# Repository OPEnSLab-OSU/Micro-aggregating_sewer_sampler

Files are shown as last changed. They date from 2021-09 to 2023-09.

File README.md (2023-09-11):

# Micro-Aggregating Sewer Sampler (MASS)
Compositing autosampler using weight based sampling targeted for sewage sampling in manholes. Code originally housed in 1232 branch of [SingleSampler repository](https://github.com/OPEnSLab-OSU/SingleSampler) and created using [Kawin Pechetratanapanit's sampler framework](https://github.com/OPEnSLab-OSU/OPEnSamplerFramework). Instructions for setting up PlatformIO within Visual Studio code are provided in the [OPEnSampler Framework Getting Started Guide](https://opensampler-framework.readthedocs.io/en/latest/pages/start_here.html). 



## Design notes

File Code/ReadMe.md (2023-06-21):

Getting Started
-----------------
This code is an application of the OPEnSamplerFramework. The easiest way to start using OPEnSamplerFramework is to use VSCode with PlatformIO extension. 
See [Getting Started Guide](https://opensampler-framework.readthedocs.io/en/latest/pages/start_here.html).

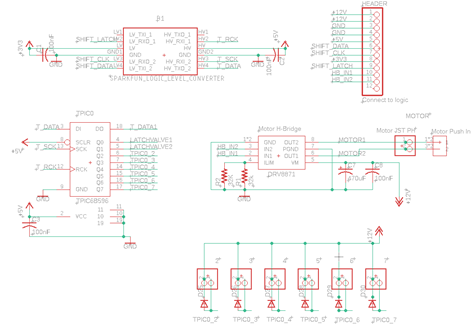
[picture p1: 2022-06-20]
DesignFiles/Power_module_schematic.png

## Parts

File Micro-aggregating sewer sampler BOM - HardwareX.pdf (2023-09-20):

Designator | Component | Number | Cost per unit $

Minimum
purchase
quantity

Total
cost $

Source of
materials

Material
type
| | Enclosures - Device
Cooler | 10 gal watercooler | 1 | $49.89 | 1 | $49.89 | Homedepot (https://www.homedepot.com/p/The-Home-Depot-10-Gal-Orange-Water-Cooler-FG1610HDORAN/202260809?) | Other
Tube holder | 3D printed tube holder | 1 | $0.19 | 1 | $0.19 | Zenodo (https://doi.org/10.5281/zenodo.8333206) | Polymer
Epoxy | Loctite 1919324 Marine Epoxy | 1 | $7.74 | 1 | $7.74 | Amazon (https://www.amazon.com/dp/B00KH62K50?amp&amp) | Polymer
Corner Brace | 2 in galvanized corner brace with screws | 4 | $1.62 | 4 | $6.46 | Home Depot (https://www.homedepot.com/p/Everbilt-2-in-Galvanized-Corner-Brace-4-Pack-15267/202033914) | Metal
Star drive screw | 3/4" 18-8 stainless steel screw | 8 | $0.42 | 25 | $10.59 | Amazon (https://www.amazon.com/Stainless-Thread-Rolling-Plastic-Passivated/dp/B00GDYW2TY) | Metal
1/2" PVC coupler | 1/2" schedule 40 PVC coupler | 1 | $0.67 | 1 | $0.67 | Home Depot (https://www.homedepot.com/p/Charlotte-Pipe-1-2-in-PVC-Schedule-40-S-x-S-Coupling-PVC021000600HD/203811331) | Polymer
Buckles | Adjustable Quick Side Release Buckles | 2 | $1.05 | 4 | $4.21 | Amazon (https://www.amazon.com/gp/product/B07N6B4CR5/ref=ppx_yo_dt_b_search_asin_title?ie=UTF8&psc=1) | Polymer
Webbing | Heavyweight Polypropylene Webbing 2 inch | 1 | $1.22 | 30 ft | $36.57 | Amazon (https://www.amazon.com/gp/product/B01KTVCGJ2/ref=ppx_yo_dt_b_search_asin_title?ie=UTF8&psc=1) | Polymer
Drawer slides | Heavy Duty Drawer Slides 14 inch | 2 | $28.40 | 2 | $56.80 | Amazon (https://www.amazon.com/AOLISHENG-Bearing-Capacity-Extension-Runners/dp/B08BKPTFQ7) | Composite
L bracket | Aluminum 90° Angle - 3.5" height, 1/4" thick | 1 | $21.27 | 1 | $21.27 | McMaster Carr (https://www.mcmaster.com/8982K137-8982K276/) | Metal
5 mm washers | 5 mm Stainless Steel Washers | 8 | $0.31 | 4 | $2.50 | Home Depot (https://www.homedepot.com/p/Everbilt-5-mm-Stainless-Steel-Flat-Washer-4-Pieces-01228/202209491) | Metal
Flathead bolt | M5, 16 mm long bolt | 6 | $0.24 | 100 | $24.00 | McMaster Carr (https://www.mcmaster.com/91430A326/) | Metal
Lock nut | M5 lock nut | 6 | $0.63 | 2 | $3.75 | Home Depot (https://www.homedepot.com/p/Everbilt-M5-0-8-Stainless-Steel-Lock-Nut-2-Pieces-D42-H-837181/321071796) | Metal
Acrylic Sheet | Acrylic - clear 24" x 24", 1/8" | 1 | $26.08 | 1 | $26.08 | McMaster Carr (https://www.mcmaster.com/8560K259/) | Polymer
Large ice pack | Reusable Ice Pack, 1 Large | 3 | $7.38 | 4 | $29.52 | Amazon (https://www.amazon.com/dp/B07YX7TCJP/ref=twister_B07YX7T91Y?_encoding=UTF8&th=1) | Composite
Medium ice pack | Reusable Ice Pack, 1 Medium | 2 | $3.79 | 4 | $15.16 | Amazon (https://www.amazon.com/dp/B07YX7TCJP/ref=twister_B07YX7T91Y?_encoding=UTF8&th=1) | Composite
Cable with carabiner | Stainless Steel Safety Cable Lock | 3 | $2.40 | 4 | $7.19 | Amazon (https://www.amazon.com/Stainless-Ekunbuy-Security-Carabiner-Flexible/dp/B08GZ6PDGY) | Metal
1/8" wire rope | Stainless steel wire rope, 1/8" | 1 | $0.54 | 33 ft | $17.88 | Amazon (https://www.amazon.com/Railing-VIGRUE-Stainless-Aluminum-Sleeves/dp/B08HN1J894) | Metal
Battery | 12 Volt 7.2 Ah SLA battery | 1 | $17.50 | 1 | $17.50 | Amazon (https://www.amazon.com/ML7-12-Battery-Mighty-Brand-Product/dp/B00K8V30D0) | Other
Quick-Disconnect Terminal | Quick-Disconnect Terminal | 2 | $1.08 | 1 | $2.16 | McMaster Carr (https://www.mcmaster.com/72625K21/) | Composite
Paracord | 1/8" x 50 ft paracord | 1 | $0.11 | 50 ft | $5.48 | Home Depot (https://www.homedepot.com/p/Everbilt-1-8-in-x-50-ft-Assorted-Color-Paracord-Rope-MFP350/205517109) | Polymer
Hydraulics - Pump
Peristaltic Pump | Peristaltic Pump DC 6Vto 24V | 1 | $54.64 | 1 | $54.64 | Aliexpress (https://www.aliexpress.com/item/4001286485389.html?spm=a2g0s.9042311.0.0.87964c4dVvskfj) | Other
Pump tubing | Hi-Temp Silicone Rubber Tubing | 1 | $1.39 | 10 ft | $13.90 | McMaster Carr (https://www.mcmaster.com/5236K891/) | Polymer
Tube to hose stem | 3/8" to 3/8" Tube To Hose Stem | 1 | $2.39 | 10 | $23.93 | Home Depot (https://www.homedepot.com/p/John-Guest-3-8-in-Push-to-Connect-Tube-to-Hose-Stem-Fitting-10-Pack-PP251212W/206940472) | Polymer
Cable tie | Cable tie, 0.1" width, 4" length | 2 | $0.04 | 100 | $3.59 | McMaster Carr (https://www.mcmaster.com/7130K52/) | Polymer
Elbow push-to-connect | 3/8 OD x 3/8 OD elbow push-to-connect | 1 | $1.30 | 10 | $12.99 | Amazon (https://www.amazon.com/dp/B07NQ8BXP3?s=hi&sp_csd=d2lkZ2V0TmFtZT1zcF9kZXRhaWw) | Composite

Designator | Component | Number | Cost per unit $ | Minimum purchase quantity | Total cost $ | Source of materials | Material type
Elbow barbed | Barbed elbow, 3/8" OD | 1 | $1.02 | 1 | $1.02 | McMaster Carr (https://www.mcmaster.com/5463K596-2974K237/?s=barbed+fittings) | Polymer
3/8" tubing | Soft ND-100-65 Tygon PVC Tubing | 1 | $93.00 | 25 ft | $93.00 | McMaster Carr (https://www.mcmaster.com/8349T26/) | Polymer
Small snap-grip clamps | Snap-Grip Clamp 29/64" to 9/16" Clamp ID | 2 | $0.46 | 25 | $11.40 | McMaster-Carr (https://www.mcmaster.com/5246K84/) | Polymer
Faraday Fabric | EMF shielding Film | 1 | $23.00 | 44"W x 36"L | $23.00 | Amazon (https://www.amazon.com/Shielding-Bluetooth-Blocking-Military-Conductive/dp/B01M294MGK) | Other
Electrical tape | Electrical tape | 1 | $5.98 | 66 ft | $5.98 | Home Depot (https://www.homedepot.com/p/Scotch-Super-33-3-4-in-x-66-ft-x-0-007-in-Vinyl-Electrical-Tape-Black-6132-BA-10/304653556) | Polymer
M3 bolt - 16 mm | 16mm M3 screw low profile | 9 | $0.13 | 100 | $13.16 | McMaster Carr (https://www.mcmaster.com/90666A107/) | Metal
M3 washer - 9 mm | 18-8 Stainless Steel Oversized Washer M3 | 13 | $0.05 | 100 | $4.93 | McMaster Carr (https://www.mcmaster.com/91116A120/) | Metal
M3 nuts | M3 nuts stainless steel | 9 | $0.06 | 50 | $3.03 | McMaster Carr | Metal
Barbed tee fitting | Barbed tee fitting, 3/8" OD | 1 | $1.40 | 10 | $13.95 | McMaster Carr (https://www.mcmaster.com/5463K608-2974K249/) | Polymer
Quick-Disconnect Plug to 3/8" barbed | Plug, 1/4 Size, for 3/8" Barbed Tube ID | 1 | $4.11 | 1 | $4.11 | McMaster Carr (https://www.mcmaster.com/5923K72/) | Polymer
Quick-Disconnect Socket to 3/8" barbed | Socket, 1/4 Size, for 3/8" Barbed Tube ID | 1 | $5.58 | 1 | $5.58 | McMaster Carr (https://www.mcmaster.com/5923K42/) | Polymer
Polyethylene tubing | Polyethylene Tube, Shore D: 45, 1/4 in ID | 1 | $4.10 | 10 ft | $4.10 | Grainger (https://www.grainger.com/product/USA-SEALING-Tubing-Polyethylene-55YU87?searchQuery=55YU87&searchBar=true) | Polymer
Tee push-to-connect | 3/8" OD Tee push-to-connect | 1 | $1.10 | 10 | $10.99 | Amazon (https://www.amazon.com/Tailonz-Pneumatic-Plastic-Connect-Fittings/dp/B07R2CQKKJ?c=ts&rnid=23957419011&s=industrial&ts_id=580146011) | Composite
Hydraulics - Valves
Motorized Ball valve - normally closed | Motorized Ball valve 1/4'' NPT - auto return | 2 | $38.29 | 1 | $76.58 | Amazon (https://www.amazon.com/Motorized-Valve-Stainless-U-S-Solid/dp/B06XXPZHVB) | Other
PTFE tape | PTFE tape | 1 | $0.98 | 260 in. | $0.98 | Home Depot (https://www.homedepot.com/p/Harvey-1-2-in-x-260-in-Thread-Sealing-PTFE-Plumber-s-Tape-0178503/202280370) | Polymer
Straight 3/8” push to connect to ¼ NPT | 3/8"OD push to connect x 1/4 Inch NPT | 2 | $1.80 | 10 | $17.99 | Amazon (https://www.amazon.com/dp/B07PN3P2PN/ref=twister_B08DR6ZB7S?_encoding=UTF8&psc=1) | Composite
Barbed 3/8" elbow to 1/4" NPT Male | Barbed elbow 3/8" ID x 1/4 NPT Male | 1 | $2.73 | 1 | $2.73 | McMaster Carr (https://www.mcmaster.com/5047K37/) | Polymer
Elbow 3/8" push-to-connect to 1/4" NPT | 3/8 OD elbow push-to-connect to 1/4 NPT | 1 | $1.88 | 5 | $9.39 | Amazon (https://www.amazon.com/Metalwork-Plastic-Nickel-Connect-Fitting/dp/B07F8YZ456) | Composite
Valve bracket | 3D printed valve bracket | 2 | $0.41 | 1 | $0.81 | Zenodo (https://doi.org/10.5281/zenodo.8333206) | Polymer
Large snap-grip clamps | Snap-Grip Clamp 37/64" to 41/64" Clamp ID | 1 | $0.49 | 25 | $12.17 | McMaster Carr (https://www.mcmaster.com/5246K86/) | Polymer
PVC tubing | PVC Firm tubing 1/4 ID 3/8 OD | 1 | $16.80 | 25 ft | $16.80 | McMaster Carr (https://www.mcmaster.com/1487T2/) | Polymer
Straight 3/8" push to connect fitting | Straight 3/8" push to connect fitting | 1 | $3.81 | 1 | $3.81 | McMaster Carr (https://www.mcmaster.com/5562K421/) | Composite

Hydraulics - Sample bag
Mylar Bag | 3L Mylar Bag | 1 | $0.89 | 250 | $221.80 | IMPAK (https://www.impakcorporation.com/flexible_packaging/CSP0912BG04) | Other
Threaded valved coupler | Coupler, Push In, Acetal, White | 1 | $6.08 | 1 | $6.08 | CPC (https://products.cpcworldwide.com/en_US/ProductsCat/APC/APCD10006) | Polymer
Eye bolt and nut | Eye bolt and nuts | 1 | $0.69 | 2 | $1.38 | Home Depot (https://www.homedepot.com/p/Everbilt-8-32-tpi-x-1-5-8-in-Zinc-Plated-Steel-Eye-Bolts-with-Nuts-2-Piece-per-Pack-816671/204273506) | Metal

Designator | Component | Number | Cost per unit $ | Minimum purchase quantity | Total cost $ | Source of materials | Material type
Barbed elbow coupling insert | Coupler, Push In, Acetal, White | 1 | $1.40 | 1 | $1.40 | CPC (https://products.cpcworldwide.com/en_US/ProductsCat/APC/APC23006) | Polymer
1/16" wire rope | 1/16" wire rope | 1 | $0.98 | 1 ft | $0.98 | Home Depot (https://www.homedepot.com/p/Everbilt-1-16-in-x-1-ft-Stainless-Steel-Uncoated-Wire-Rope-809786/204765202) | Metal
Compression sleeve | 1/16" Wire Rope Compression Sleeve | 1 | $0.97 | 10 | $9.69 | McMaster-Carr (https://www.mcmaster.com/3755T13/) | Metal
Load Cell Mechanical
M5 bolt | M5 bolt, 40 mm | 1 | $1.38 | 2 | $1.38 | Home Depot (https://www.homedepot.com/p/Everbilt-M5-0-8-x-40-mm-Phillips-Pan-Head-Stainless-Steel-Machine-Screw-2-Pack-843098/204283788) | Metal
Large Washer | 18 mm OD M5 washer | 2 | $0.14 | 100 | $14.29 | McMaster Carr (https://www.mcmaster.com/98363A111/) | Metal
Neoprene washer | 1/4" thick neoprene washer | 2 | $0.69 | 4 | $2.75 | Home Depot (https://www.homedepot.com/p/Everbilt-1-4-in-x-5-8-in-Black-Neoprene-Washer-4-Pieces-89188/100338046) | Polymer
Spacer | Spacer - 7 mm | 1 | $1.76 | 1 | $1.76 | McMaster Carr (https://www.mcmaster.com/94669A334/) | Metal
M5 nut | M5 stainless steel nut | 1 | $0.63 | 2 | $1.25 | Home Depot (https://www.homedepot.com/p/5-mm-8-Hex-Nut-Stainless-862608/323370947) | Metal
Enclosures - Electronics
Electronic Box | Polycarbonate waterproof box | 1 | $5.88 | 1 | $5.88 | Arrow (https://www.arrow.com/en/products/rb55p14c10g/serpac-electronic-enclosures?q=RB55P14C10G) | Polymer
RGB LED | WS2812B LED | 1 | $0.16 | 100 | $15.99 | Amazon (https://www.amazon.com/gp/product/B01D1FFVOA/ref=ppx_yo_dt_b_search_asin_title?ie=UTF8&psc=1) | Composite
LED box | LED 3D printed box | 1 | $0.04 | 1 | $0.04 | OPEnS | Polymer
LED lid | LED 3D printed lid | 1 | $0.05 | 1 | $0.05 | OPEnS | Polymer
3 wire cable | 3 wire cable | 1 | $0.31 | 100 ft | $31.10 | Amazon (https://www.amazon.com/Custom-Cable-Connection-Conductor-Stranded/dp/B071DFHKRB) | Composite
Super glue | Gorilla Super Glue Gel | 1 | $6.84 | 1 | $6.84 | Amazon (https://www.amazon.com/dp/B082XGL21J?amp=undefined) | Polymer
Push button | Momentary Push button waterproof | 2 | $2.20 | 5 | $10.99 | Amazon (https://www.amazon.com/gp/product/B07F9PLSRY/ref=ppx_yo_dt_b_search_asin_title?ie=UTF8&psc=1) | Composite
2 pin JST wire pairs | 2 pin JST wire pairs | 4 | $1.60 | 5 | $7.99 | Amazon (https://www.amazon.com/JST-XH-Balance-Connector-Silicone-Woodland/dp/B07YKHV46N?cv_ct_cx=jst-xh+wire+2+pin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) | Composite
Small heat shrink | Small heat shrink | 4 | $0.01 | 580 | $6.59 | Amazon (https://www.amazon.com/gp/product/B01MFA3OFA/ref=ppx_yo_dt_b_search_asin_title?ie=UTF8&psc=1) | Polymer
Solder seal connectors | Solder Seal Wire Connectors 22-18 AWG | 4 | $0.20 | 50 | $9.99 | Amazon (https://www.amazon.com/gp/product/B07C3MKM3K/ref=ppx_yo_dt_b_search_asin_title?ie=UTF8&th=1) | Composite
PG7 cable gland | PG7 cable gland | 1 | $1.52 | 1 | $1.52 | Mouser (https://www.mouser.com/ProductDetail/Hammond-Manufacturing/1427NCGPG7B?qs=sGAEpiMZZMvSvAwuKVmiP9gF42NFqy3rmTmaMc262xA%3D) | Polymer
PG13.5 cable gland | PG13.5 cable gland | 1 | $1.89 | 1 | $1.89 | Mouser (https://www.mouser.com/ProductDetail/Hammond-Manufacturing/1427NCGPG13B?qs=l4Gc20tDgJJFw57NH75JRw%3D%3D) | Polymer
Power plug | Right Angle Power Plug Jack to Bare Wire | 1 | $1.60 | 10 | $15.99 | Amazon (https://www.amazon.com/gp/product/B0851CV1Y6/ref=ppx_yo_dt_b_search_asin_title?ie=UTF8&psc=1) | Composite
microUSB cable | Right angle microUSB cable | 1 | $5.58 | 1 | $5.58 | DigiKey (https://www.digikey.com/en/products/detail/qualtek/3021079-06/8681882) | Other
Stranded wire: black, red, white, green | 22 AWG Gauge Stranded Wire, 6 colors | 1 | $1.25 | 6 rolls at 5 ft | $7.50 | Amazon (https://www.amazon.com/Fermerry-Stranded-Electrical-Silicone-Cables/dp/B089CQ2N69) | Composite
Power Module PCB Components
Power module PCB | Power module mini PCB | 1 | $2.30 | 5 | $11.50 | Zenodo (https://doi.org/10.5281/zenodo.8333206) | Composite
Logic level converter | Sparkfun logic level shifter | 1 | $2.95 | 1 | $2.95 | Sparkfun (https://www.sparkfun.com/products/12009) | Composite

Designator | Component | Number | Cost per unit $ | Minimum purchase quantity | Total cost $ | Source of materials | Material type
12 pin angle female header | 12 pins angle female header | 1 | $0.80 | 1 | $0.80 | DigiKey (https://www.digikey.com/product-detail/en/sullins-connector-solutions/PPTC121LGBN-RC/S5448-ND/775906) | Composite
32K resistor | Resistor 32K Ohm 3.3mm | 1 | $0.10 | 1 | $0.20 | DigiKey (https://www.digikey.com/product-detail/en/stackpole-electronics-inc/CF18JT33K0/CF18JT33K0CT-ND/2022778) | Other
470uF capacitor | Capacitor 470uF SMD 16V | 1 | $0.51 | 1 | $0.51 | DigiKey (https://www.digikey.com/product-detail/en/nichicon/UWT1C471MNL1GS/493-2181-1-ND/590156) | Other
100 nF capacitor | Capacitor 100nF SMD | 4 | $0.12 | 1 | $0.48 | DigiKey (https://www.digikey.com/product-detail/en/samsung-electro-mechanics/CL31B104KBCNNNC/1276-1017-1-ND/3889103) | Other
Flyback Diode | Diode Standard 100V 150 mA | 2 | $0.15 | 1 | $0.30 | DigiKey (https://www.digikey.com/product-detail/en/diodes-incorporated/1N4148W-7-F/1N4148W-FDICT-ND/815280) | Other
Shift register | IC Power 8-bit shift Register 20-SOIC | 1 | $1.42 | 1 | $5.68 | DigiKey (https://www.digikey.com/product-detail/en/texas-instruments/TPIC6B595DWR/296-1351-1-ND/404964) | Other
Relay | 1 Channel DC 5V Relay Module | 1 | $1.75 | 1 | $6.99 | Amazon (https://www.amazon.com/gp/product/B095YD3732/ref=ppx_yo_dt_b_search_asin_title?ie=UTF8&psc=1) | Other
Standoff | M3 standoff | 1 | $2.17 | 1 | $2.17 | McMaster Carr (https://www.mcmaster.com/98952A112/) | Metal
M3 6 mm bolt | M3 6 mm bolt | 1 | $0.05 | 50 | $2.51 | Grainger (https://www.grainger.com/product/GRAINGER-APPROVED-Socket-Head-Cap-Screw-M3-0-22TY43) | Metal
Rectifier Diode | Rectifiers Diode, DO-41, 50V, 1A | 1 | $0.40 | 1 | $0.40 | Mouser (https://www.mouser.com/ProductDetail/Diotec-Semiconductor/1N4001?qs=OlC7AqGiEDlll8NA510wmA%3D%3D) | Other
Logic Module Components
Logic pcb | Logic Module PCB | 1 | $2.30 | 5 | $11.50 | Zenodo (https://doi.org/10.5281/zenodo.8333206) | Composite
M0 female header | Feather M0 header female | 1 | $0.95 | 1 | $0.95 | Adafruit (https://www.adafruit.com/product/2886) | Composite
Angle male header | Angle male header 2.54 mm | 12 | $0.02 | 1 | $0.24 | DigiKey (https://www.digikey.com/products/en?keywords=HDR100IMP40M-G-RA-TH-ND) | Composite
MicroSD mount | MicroSD card mount SMD - Hinged type | 1 | $1.16 | 1 | $1.16 | DigiKey (https://www.digikey.com/product-detail/en/molex/0472192001/WM6698CT-ND/3044147) | Metal
MicroSD card | 16 GB microSD card with adapter | 1 | $7.99 | 1 | $7.99 | Amazon (https://www.amazon.com/gp/product/B004ZIENBA/ref=ox_sc_act_title_1?smid=ATVPDKIKX0DER&psc=1) | Other
Coin cell battery holder | 12mm Battery holder | 1 | $1.30 | 1 | $1.30 | DigiKey (https://www.digikey.com/product-detail/en/mpd-memory-protection-devices/BC501SM-TR/BC501SM-TRCT-ND/5418194) | Metal
Coin cell battery | CR1220 | 1 | $0.52 | 1 | $0.52 | Grainger (https://www.grainger.com/product/GRAINGER-APPROVED-1220-54ZU79) | Other
Barrel jack | Power Barrel Connector Jack Surface Mount | 1 | $1.32 | 1 | $1.32 | DigiKey (https://www.digikey.com/product-detail/en/cui-inc/PJ-002AH-SMT-TR/CP-002AHPJCT-ND/669692) | Composite
Switch | Slide switch DPDT 300MA 6V | 1 | $0.55 | 1 | $0.55 | DigiKey (https://www.digikey.com/product-detail/en/c-k/JS202011JCQN/CKN10723CT-ND/6137637) | Composite
RTC | RTC I2C 16-SOIC DS3231 | 1 | $9.78 | 1 | $9.78 | DigiKey (https://www.digikey.com/en/products/detail/maxim-integrated/DS3231SN-T-R/1197577) | Other
P-channel MOSFET | P-channel MOSFET 130mA | 1 | $0.27 | 1 | $0.27 | DigiKey (https://www.digikey.com/product-detail/en/diodes-incorporated/BSS84-7-F/BSS84-FDICT-ND/717844) | Other
Not-Gate | Inverter IC 1 Channel - SOT-23-5 | 1 | $0.34 | 1 | $0.34 | DigiKey (https://www.digikey.com/en/products/detail/texas-instruments/SN74AHC1G04DBVR/276357) | Other
D Flipflop | D Flip Flop SOT23-6 | 1 | $0.37 | 1 | $0.37 | DigiKey (https://www.digikey.com/product-detail/en/texas-instruments/SN74LVC1G175DBVR/296-17617-1-ND/706599) | Other
Zener Diode | Zener Diode 4.3 V 800 mW - Surface Mount | 1 | $0.44 | 1 | $0.44 | DigiKey (https://www.digikey.com/en/products/detail/vishay-semiconductor-diodes-division/BZD27C4V3P-E3-08/6680647) | Other
Diode Schottky | Diode Schottky 1A (DC) Surface Mount | 1 | $0.39 | 1 | $0.39 | DigiKey (https://www.digikey.com/en/products/detail/onsemi/NSR0320MW2T1G/1218949) | Other
Inductor | Inductor 10uH 2,7A | 1 | $1.69 | 1 | $1.69 | DigiKey (https://www.digikey.com/product-detail/en/wurth-electronics-inc/74438357100/732-11206-1-ND/6833665) | Other
Linear regulator | Buck regulator | 1 | $2.77 | 1 | $2.77 | TI (https://www.ti.com/product/LMR16006Y-Q1/part-details/LMR16006YQ5DDCRQ1?keyMatch=LMR16006YQ5DDCRQ1&tisearch=search-everything&usecase=OPN&login-check=true) | Other

Designator | Component | Number | Cost per unit $ | Minimum purchase quantity | Total cost $ | Source of materials | Material type
Red LED | KingBright Red LED low current 0805 | 1 | $0.51 | 1 | $0.51 | DigiKey (https://www.digikey.com/product-detail/en/kingbright/APT2012LSECK-J3-PRV/754-1935-1-ND/5177465) | Other
Yellow LED | KingBright Yellow LED low current 0805 | 1 | $0.51 | 1 | $0.51 | DigiKey (https://www.digikey.com/product-detail/en/lite-on-inc/LTL-4291N/160-1968-ND/3198548) | Other
3K resistor | Resistor 3K Ohm resistor 1% | 1 | $0.10 | 1 | $0.10 | DigiKey | Other
6.2K resistor | Resistor 6.2K Ohm 1% 1206 | 1 | $0.10 | 1 | $0.10 | DigiKey (https://www.digikey.com/product-detail/en/yageo/RC1206FR-076K2L/311-6.20KFRCT-ND/731963) | Other
10K resistor | Resistor 10k Ohm 1% 1206 | 3 | $0.10 | 1 | $0.30 | DigiKey (https://www.digikey.com/product-detail/en/te-connectivity-passive-product/CRGCQ1206J10K/A130183CT-ND/8578015) | Other
10K through hole resistor | 10k Ohm through hole resistor 1% | 2 | $0.10 | 1 | $0.20 | DigiKey (https://www.digikey.com/en/products/detail/stackpole-electronics-inc/RNMF14FTC10K0/1683930) | Other
39K resistor | Resistor 39K Ohm 5% 1206 | 1 | $0.10 | 1 | $0.10 | DigiKey (https://www.digikey.com/product-detail/en/yageo/RC1206JR-0739KL/311-39KERCT-ND/732237) | Other
100K resistor | Resistor 100K Ohm 1% 1206 | 1 | $0.10 | 1 | $0.10 | DigiKey (https://www.digikey.com/product-detail/en/yageo/RC1206FR-07100KL/311-100KFRCT-ND/731439) | Other
300K resistor | Resistor 300K Ohm 0.1% 1206 | 1 | $0.66 | 1 | $0.66 | DigiKey (https://www.digikey.com/product-detail/en/panasonic-electronic-components/ERA-8AEB304V/P300KBCCT-ND/3069731) | Other
1M resistor | Resistor 1M Ohm 0.1% 1206 | 1 | $0.62 | 1 | $0.62 | DigiKey (https://www.digikey.com/product-detail/en/stackpole-electronics-inc/RNCS1206BKE1M00/RNCS1206BKE1M00CT-ND/1801449) | Other
0.1uF 1206 capacitor | Capacitor 0.1uF 100V 1206 | 5 | $0.19 | 1 | $0.95 | DigiKey (https://www.digikey.com/en/products/detail/yageo/CC1206KKX7R0BB104/2833794) | Other
10uF 1206 capacitor | Capacitor 10uF 25V 1206 | 1 | $0.22 | 1 | $0.22 | DigiKey (https://www.digikey.com/product-detail/en/samsung-electro-mechanics/CL31A106KAHNNNE/1276-1075-1-ND/3889161) | Other
47uF 1206 capacitor | Capacitor 47uF 10V 1206 | 1 | $0.69 | 1 | $0.69 | DigiKey (https://www.digikey.com/product-detail/en/samsung-electro-mechanics/CL31A476MPHNNNE/1276-3063-1-ND/3891149) | Other
30k ohm resistor | 30k ohm resistor 5% | 1 | $0.10 | 1 | $0.10 | DigiKey (https://www.digikey.com/product-detail/en/panasonic-electronic-components/ERJ-8GEYJ303V/P30KECT-ND/203313) | Other
Load Cell Circuit
ADS1232 | 24-bit ADC | 1 | $16.99 | 1 | $16.99 | Amazon (https://www.amazon.com/NOYITO-ADS1232-Digital-Converter-Arduino/dp/B07PQW6W1L) | Other
ADS1232 interface PCB | ADS1232 interface PCB | 1 | $3.83 | 3 | $11.49 | Zenodo (https://doi.org/10.5281/zenodo.8333206) | Other
4 position terminal block | Terminal Block 4 Position Top Entry 2.54mm | 1 | $1.52 | 1 | $1.52 | DigiKey (https://www.digikey.com/en/products/detail/te-connectivity-amp-connectors/1-2834015-4/5872943) | Composite
Female Header Set | 12-pin and 16-pin Female Header Set | 1 | $0.95 | 1 | $0.95 | Adafruit (https://www.adafruit.com/product/2886) | Composite
Ferrite Bead | Ferrite Bead 300 Ohm 0805 1LN | 2 | $0.19 | 1 | $0.38 | DigiKey (https://www.digikey.com/en/products/detail/laird-signal-integrity-products/MI0805L301R-10/806751) | Other
47 uF 0805 Capacitor | Capacitor Ceramic 47uF 10V X5R 0805 | 2 | $1.25 | 1 | $2.50 | DigiKey (https://www.digikey.com/en/products/detail/kyocera-avx/0805ZD476MAT2A/13981891) | Other
0.1 uF 0805 Capacitor | Capacitor Ceramic 0.1uF 10V X7R 0805 | 2 | $0.18 | 1 | $0.36 | DigiKey (https://www.digikey.com/en/products/detail/kemet/C0805C104K8RACTU/3471722) | Other
1uF X7R 0805 Capacitor | Capacitor ceramic 1uF 10V X7R 0805 | 2 | $0.29 | 1 | $0.58 | DigiKey (https://www.digikey.com/en/products/detail/kemet/C0805C105K8RACAUTO/3314925?s=N4IgTCBcDaIMwE4EFoBsC4EZnYHIBEQBdAXyA) | Other
10 Ohm resistor | Resistor SMD 10 Ohm 0.1% 1/4W 0805 | 1 | $0.96 | 1 | $0.96 | DigiKey (https://www.digikey.com/en/products/detail/stackpole-electronics-inc/RNCF0805AKT10R0/1711294) | Other
113 Ohm Resistor | Resistor SMD 113 Ohm 0.1% 1/4W 0805 | 2 | $0.69 | 1 | $1.38 | DigiKey (https://www.digikey.com/en/products/detail/te-connectivity-passive-product/2-2176091-9/4034807) | Other
Male Jumper Wires 150 mm | Male Jumper Wires 150 mm | 1 | $0.10 | 20 | $1.95 | Adafruit (https://www.adafruit.com/product/1957) | Composite
Load Cell | Micro Load Cell (0-5Kg) | 1 | $7.00 | 1 | $7.00 | Phidgets (https://www.phidgets.com/?tier=3&catid=9&pcid=7&prodid=224) | Other
Pressure Sensor

Designator | Component | Number | Cost per unit $ | Minimum purchase quantity | Total cost $ | Source of materials | Material type
Pressure sensor PCB | Pressure sensor PCB | 1 | $0.50 | 3 | $1.50 | Zenodo (https://doi.org/10.5281/zenodo.8333206) | Composite
Pressure Sensor | Pressure Sensor MS5803-02BA | 1 | $10.72 | 1 | $10.72 | DigiKey (https://www.digikey.com/product-detail/en/te-connectivity-measurement-specialties/MS580302BA01-00/223-1624-5-ND/5277629) | Other
0.1 uF Capacitor | 0.1 uF Capacitor 1206 | 1 | $0.20 | 1 | $0.20 | DigiKey (https://www.digikey.com/product-detail/en/yageo/CC1206KKX7R0BB104/311-1488-1-ND/2833794) | Other
Pressure sensor box lid | Pressure sensor box lid | 1 | $0.07 | 1 | $0.07 | Zenodo (https://doi.org/10.5281/zenodo.8333206) | Polymer
Pressure sensor box | Pressure sensor box | 1 | $0.18 | 1 | $0.18 | Zenodo (https://doi.org/10.5281/zenodo.8333206) | Polymer
4 conductor shielded wire | 4 conductor shielded wire | 1 | $5.98 | 1 m | $5.98 | DigiKey (https://www.digikey.com/en/products/detail/tensility-international-corp/30-00452/7928047) | Composite
1/4" OD polyethylene tube | Crack-Resistant Polyethylene Firm Tubing | 1 | $3.25 | 25 ft | $3.25 | McMaster Carr (https://www.mcmaster.com/5181k39) | Polymer
Conformal coating | Conformal coating | 1 | $17.00 | 1 | $17.00 | Amazon (https://www.amazon.com/MG-Chemicals-422C-Silicone-Conformal/dp/B08K9CC5LC) | Other
Feather M0
Feather M0 | Feather M0 Basic Proto | 1 | $19.95 | 1 | $19.95 | Adafruit (https://www.adafruit.com/product/2772) | Other
M0 stacking header | Feather M0 header stacking | 1 | $1.25 | 1 | $1.25 | Adafruit (https://www.adafruit.com/product/2830) | Composite
M0 female header | Feather M0 header female | 1 | $0.95 | 1 | $0.95 | Adafruit (https://www.adafruit.com/product/2886) | Composite

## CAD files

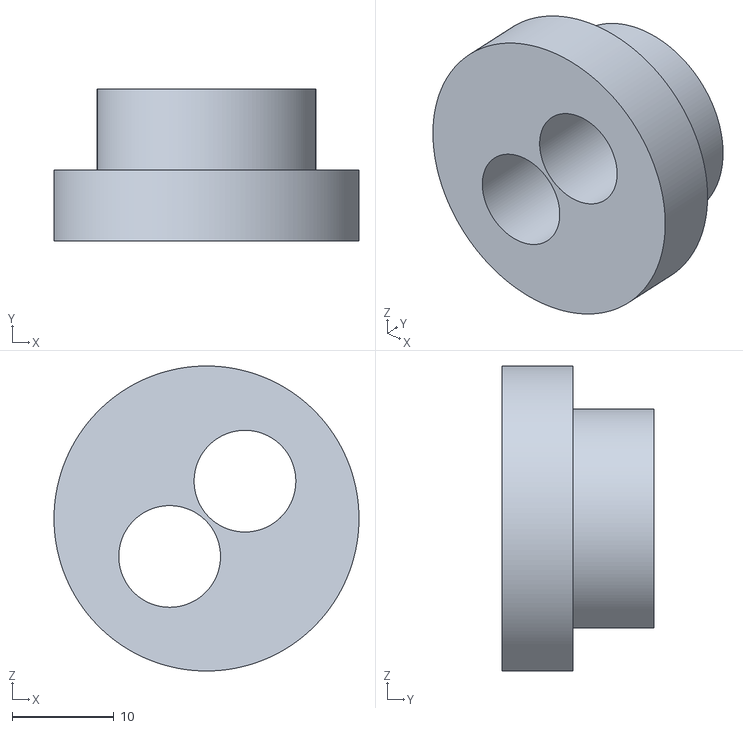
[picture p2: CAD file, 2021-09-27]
DesignFiles/Tube holder.stl
30.0 x 15.0 x 30.0

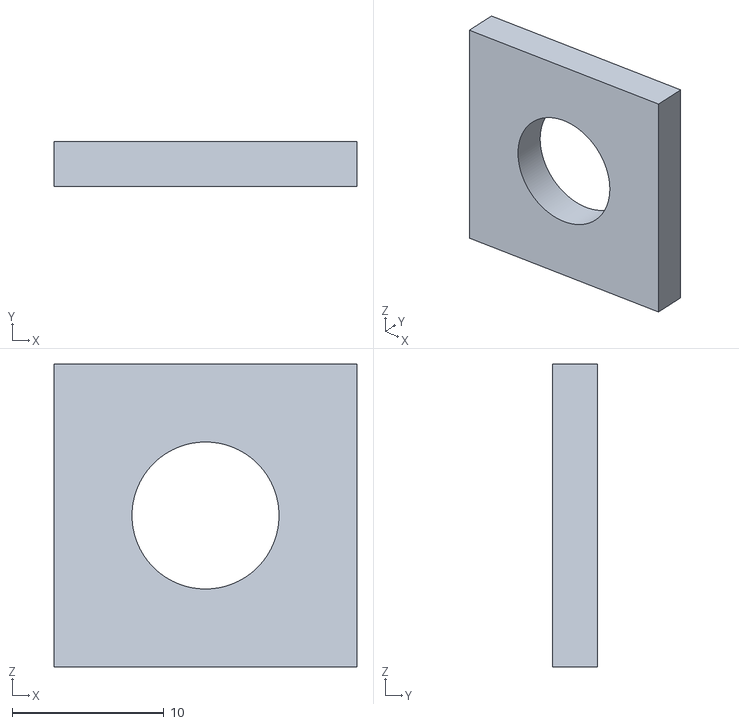
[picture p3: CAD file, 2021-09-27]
DesignFiles/LED Box.stl
20.0 x 3.00 x 20.0

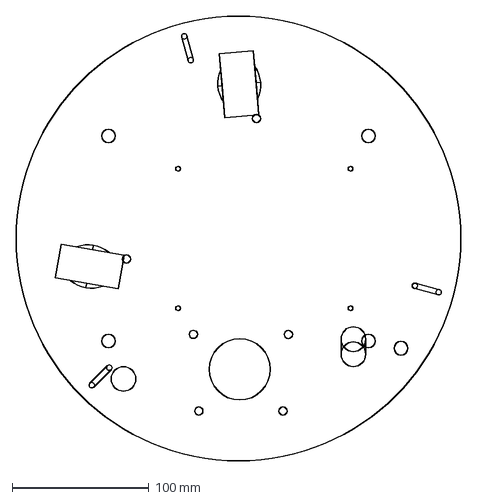
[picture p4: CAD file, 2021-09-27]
DesignFiles/AcrylicCircle.dxf
325.0 x 325.0 mm

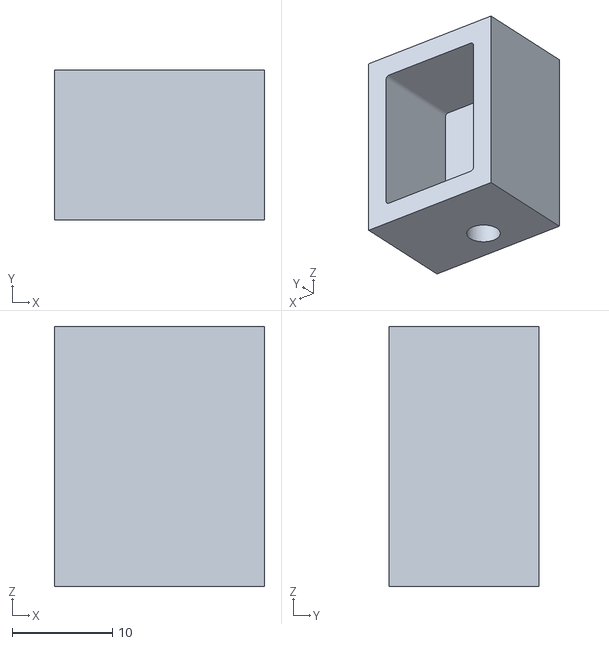
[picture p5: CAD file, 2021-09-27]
DesignFiles/pressure sensor Box.stl
21.0 x 15.0 x 26.0

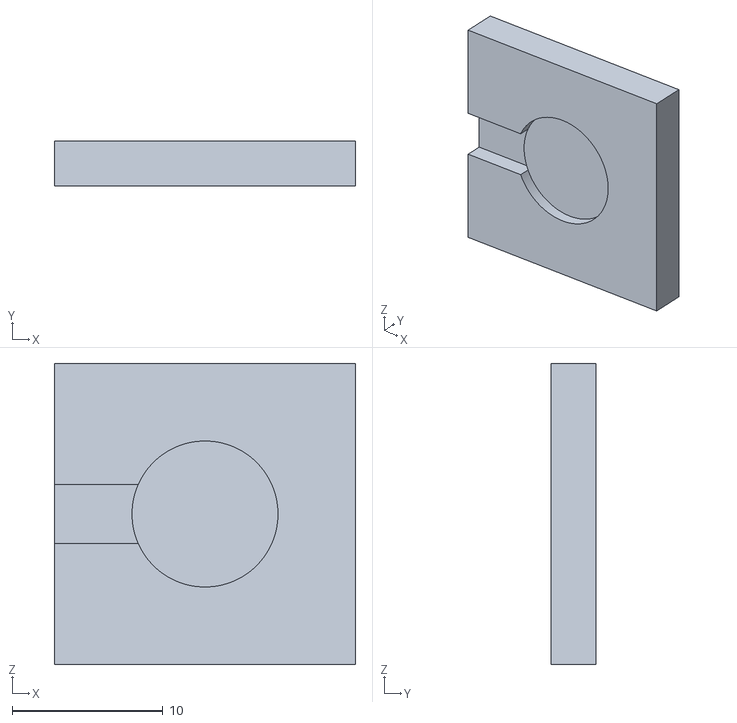
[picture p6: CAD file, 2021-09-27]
DesignFiles/LED Lid.stl
20.0 x 3.00 x 20.0

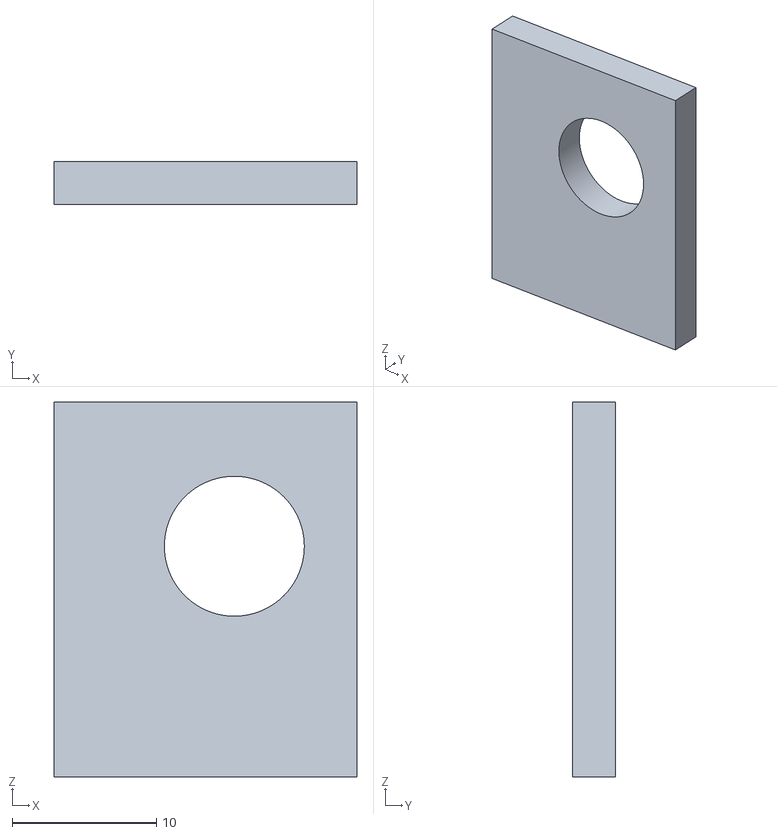
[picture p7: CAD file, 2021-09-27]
DesignFiles/pressure sensor Box lid.stl
21.0 x 3.00 x 26.0

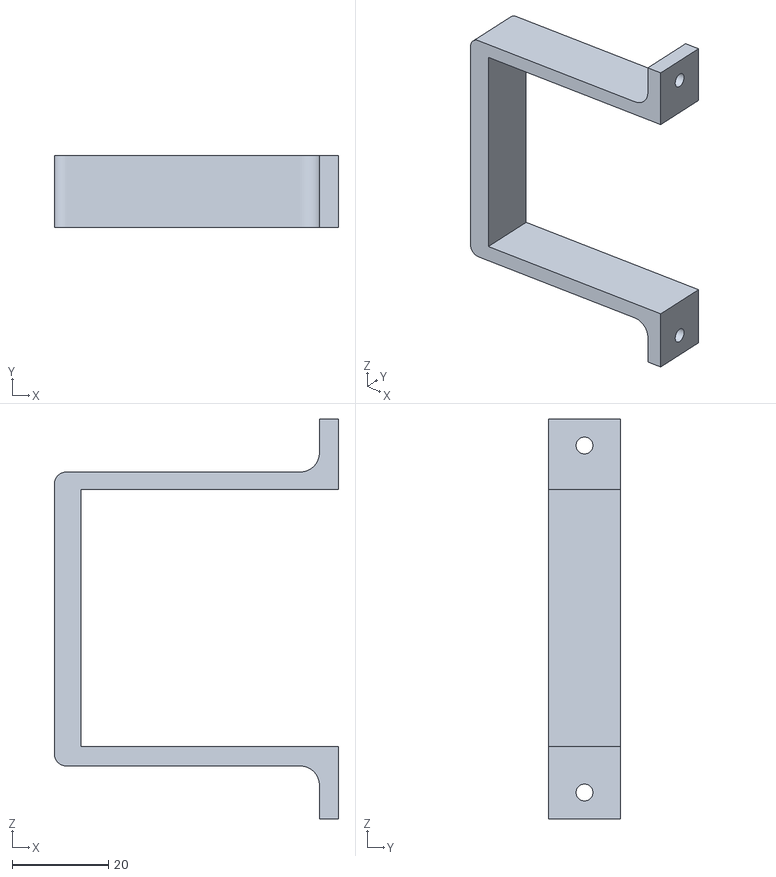
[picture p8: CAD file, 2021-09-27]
DesignFiles/Valve Bracket.stl
59.0 x 15.0 x 83.0

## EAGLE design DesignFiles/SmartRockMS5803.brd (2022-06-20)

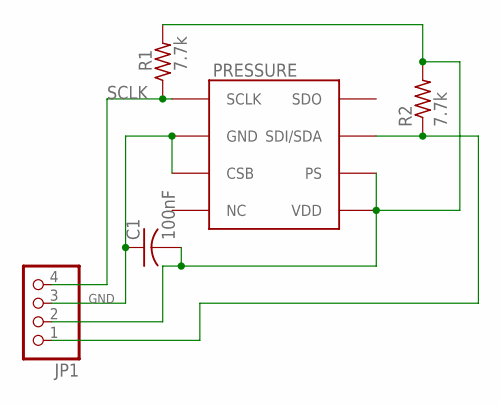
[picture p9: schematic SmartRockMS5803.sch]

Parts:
C1: 100nF; C0805
JP1: PINHD-1X4; 1X04
PRESSURE: MS5803-01BA; SMD
R1, R2: 7.7k; R0805

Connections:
GND: C1.1, JP1.3, PRESSURE.CSB, PRESSURE.GND
unnamed: C1.2, JP1.2, PRESSURE.PS, PRESSURE.VDD, R1.2, R2.2
unnamed: JP1.1, PRESSURE.SDI/SDA, R2.1
SCLK: JP1.4, PRESSURE.SCLK, R1.1

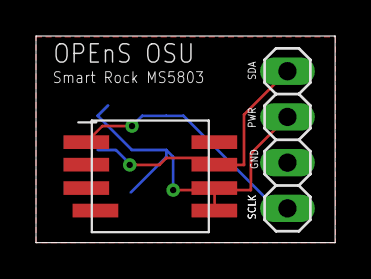
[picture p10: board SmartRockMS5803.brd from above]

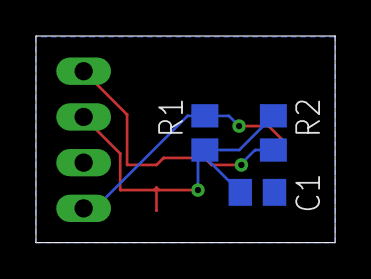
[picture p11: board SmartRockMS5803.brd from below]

Board: 2 copper layers, 16.6 x 11.5 mm, 5 parts (3 on the bottom side), 4 nets.

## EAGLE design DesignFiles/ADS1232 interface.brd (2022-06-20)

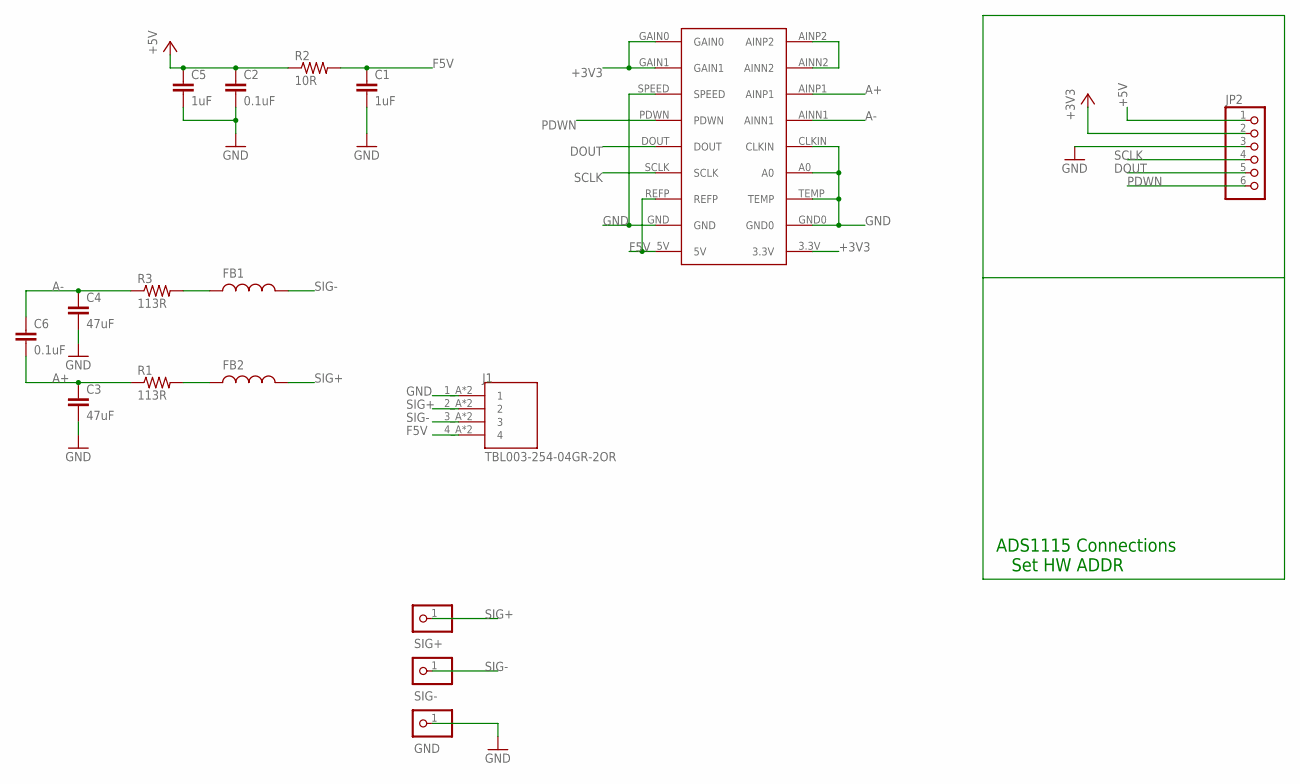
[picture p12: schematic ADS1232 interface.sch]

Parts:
ADS1232: ADS1232
C1, C5: 1uF; C0805
C2, C6: 0.1uF; C0805
C3, C4: 47uF; C0805
FB1, FB2: WE-RFI_0805A_744760282A; WE-RFI_0805A
GND: PINHD-1X1; 1X01
J1: TBL003-254-04GR-2OR; CUI_TBL003-254-04GR-2OR
JP2: PINHD-1X6; 1X06
R1, R3: 113R; R0805
R2: 10R; R0805
SIG+: PINHD-1X1; 1X01
SIG-: PINHD-1X1; 1X01

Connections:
+3V3: ADS1232.3.3V, ADS1232.GAIN0, ADS1232.GAIN1, JP2.2
+5V: C2.1, C5.1, JP2.1, R2.1
A+: ADS1232.AINP1, C3.1, C6.2, R1.1
A-: ADS1232.AINN1, C4.1, C6.1, R3.1
DOUT: ADS1232.DOUT, JP2.5
F5V: ADS1232.5V, ADS1232.REFP, C1.1, J1.4_A (4), J1.4_B (4), R2.2
GND: ADS1232.A0, ADS1232.AINN2, ADS1232.AINP2, ADS1232.CLKIN, ADS1232.GND, ADS1232.GND0, ADS1232.SPEED, ADS1232.TEMP, C1.2, C2.2, C3.2, C4.2, C5.2, GND.1, J1.1_A (1), J1.1_B (1), JP2.3
unnamed: FB1.1, R3.2
unnamed: FB2.1, R1.2
PDWN: ADS1232.PDWN, JP2.6
SCLK: ADS1232.SCLK, JP2.4
SIG+: FB2.2, J1.2_A (2), J1.2_B (2), SIG+.1
SIG-: FB1.2, J1.3_A (3), J1.3_B (3), SIG-.1

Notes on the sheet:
ADS1115 Connections Set HW ADDR

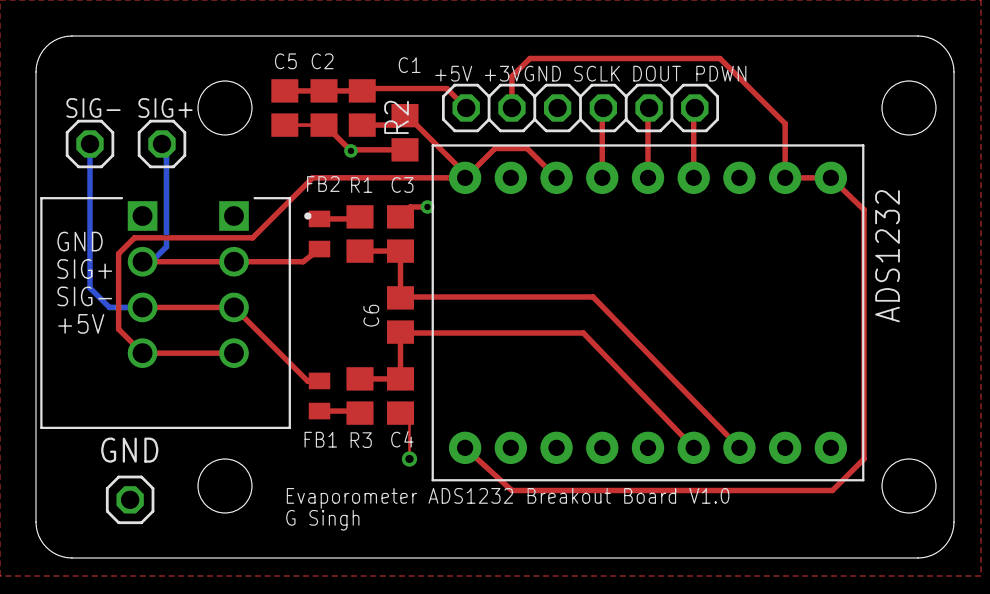
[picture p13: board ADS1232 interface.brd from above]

Board: 2 copper layers, 51.0 x 29.0 mm, 17 parts (0 on the bottom side), 13 nets.

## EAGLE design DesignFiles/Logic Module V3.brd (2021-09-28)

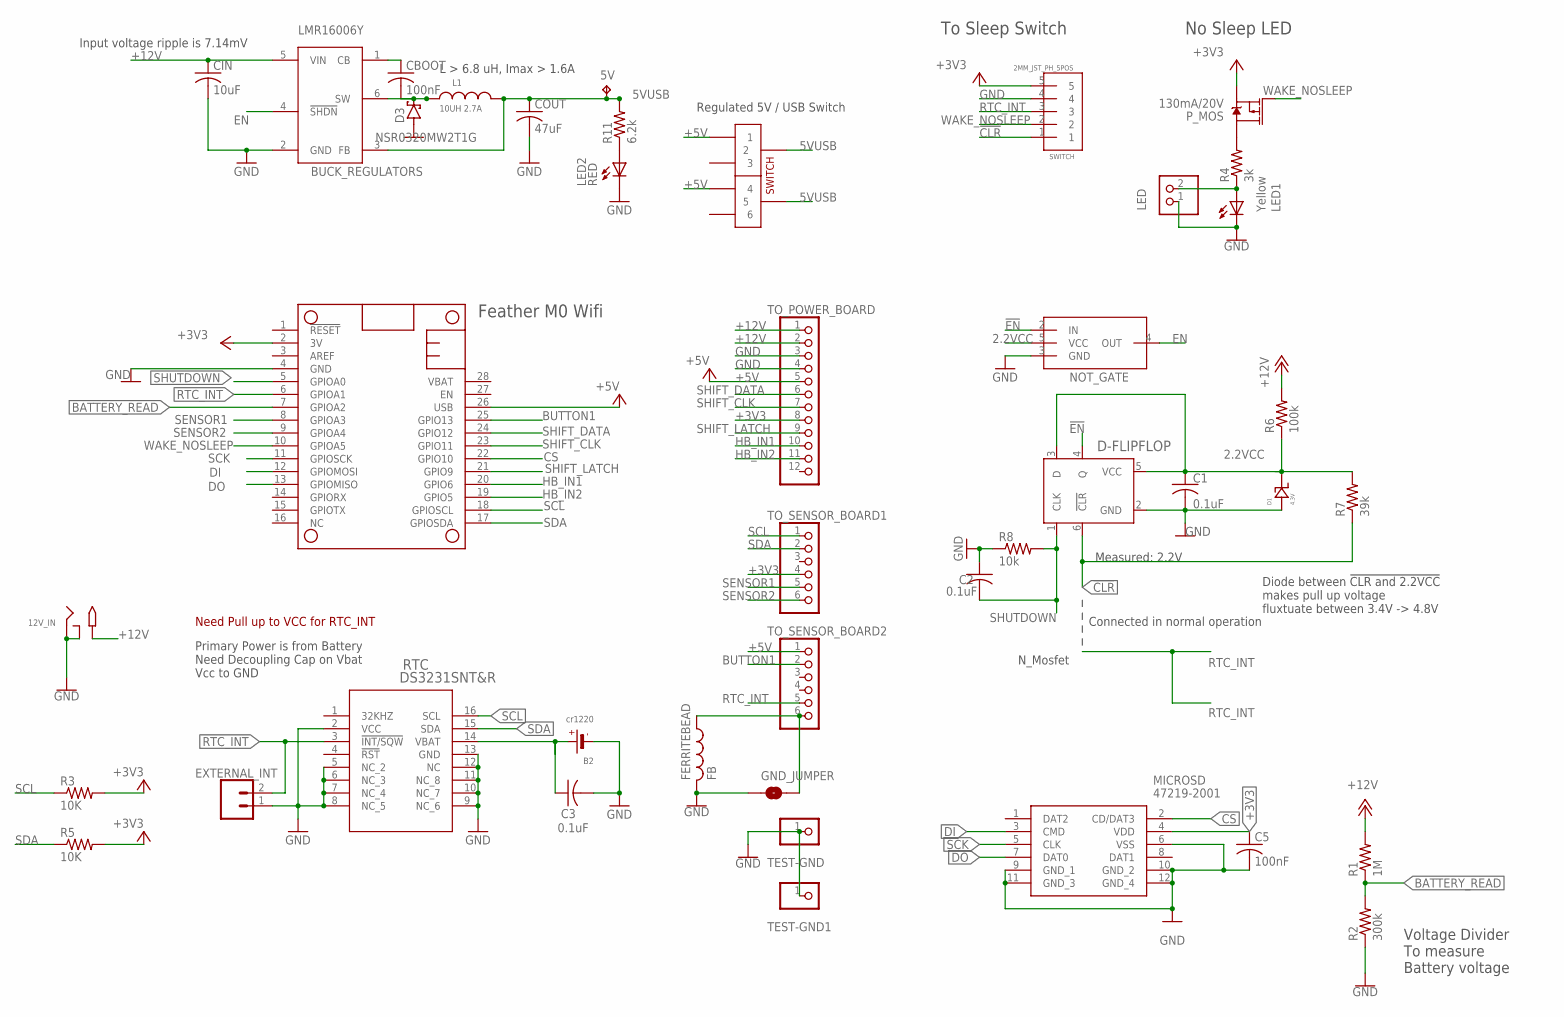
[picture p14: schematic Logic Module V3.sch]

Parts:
5V: TPTP16R; TP16R
12V_IN: 2.1MMJACKSMT; DCJACK_2MM_SMT
B2: cr1220; CR1220-2
C1, C2, C3: 0.1uF; C1206
C5: 100nF; C1206
CBOOT: 100nF; C1206
CIN: 10uF; C1206K
COUT: 47uF; C1206
D1: 4.3V; DO-219AC
D3: NSR0320MW2T1G; SOD323_ST
D-FLIPFLOP: SN74LVC1G175DBVR; DBV6
EXTERNAL_INT: CONN_021X02_NO_SILK; 1X02_NO_SILK
FERRITEBEAD: FB
GND_JUMPER: JUMPER-SMT_2_NO_NO-SILK; SMT-JUMPER_2_NO_NO-SILK
L1: 10UH 2.7A; WE-MAPI_40XX
LED: 2.5MM_JST_UP_2POS; JST_2POS_2.5MM_UP
LED1: Yellow; CHIPLED_0805
LED2: RED; CHIPLED_0805
MICROSD: 47219-2001; 472192001
MS1: FEATHERWING
P_MOS: 130mA/20V; SOT23-3
R1: 1M; R1206
R2: 300k; R1206
R3, R5: 10K; R1206
R4: 3k; R1206
R6: 100k; R1206
R7: 39k; R1206
R8: 10k; R1206
R11: 6.2k; RES_1206
RTC: DS3231SNT&R; 21-0042B_16
SWITCH: 2MM_JST_PH_5POS; 2MM_5POS_HEADER
TEST-GND, TEST-GND1: PINHD-1X1; 1X01
TO_POWER_BOARD: PINHD-1X12; 1X12
TO_SENSOR_BOARD1, TO_SENSOR_BOARD2: PINHD-1X6CB; 1X06-CLEANBIG
U$1: 2PDT_SWITCHJS-SMD; JS-DPDT-SMD
U$3: NOT_GATE; SOT753
VREG: BUCK_REGULATORS; SOT23-6

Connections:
2.2VCC: C1.1, D1.FNT, D-FLIPFLOP.3 (D), D-FLIPFLOP.5 (VCC), R6.1, R7.2, U$3.5 (VCC)
5VUSB: 5V.TP, COUT.1, L1.2, R11.2, U$1.P$2 (2), U$1.P$5 (5), VREG.3 (FB)
!CLR: D-FLIPFLOP.6 (!CLR), R7.1, SWITCH.1
!EN: D-FLIPFLOP.4 (Q), U$3.2 (IN)
+3V3: C5.1, MICROSD.4 (VDD), MS1.2 (3V), P_MOS.2 (S), R3.2, R5.2, SWITCH.5, TO_POWER_BOARD.8, TO_SENSOR_BOARD1.4
+5V: MS1.26 (USB), TO_POWER_BOARD.5, TO_SENSOR_BOARD2.1, U$1.P$1 (1), U$1.P$4 (4)
+12V: 12V_IN.PWR2 (TIP), CIN.1, R1.2, R6.2, TO_POWER_BOARD.1, TO_POWER_BOARD.2, VREG.5 (VIN)
BATTERY_READ: MS1.7 (GPIOA2), R1.1, R2.2
BUTTON1: MS1.25 (GPIO13), TO_SENSOR_BOARD2.2
CS: MICROSD.2 (CD/DAT3), MS1.22 (GPIO10)
DI: MICROSD.3 (CMD), MS1.12 (GPIOMOSI)
DO: MICROSD.7 (DAT0), MS1.13 (GPIOMISO)
EN: U$3.4 (OUT), VREG.4 (!SHDN)
GND: 12V_IN.GND (RING), 12V_IN.GNDBREAK (RING_SW), B2.-, C1.2, C2.1, C3.2, C5.2, CIN.2, COUT.2, D1.BCK, D3.A, D-FLIPFLOP.2 (GND), EXTERNAL_INT.1, FERRITEBEAD.P$2 (2), GND_JUMPER.1, LED.1, LED1.C, LED2.C, MICROSD.6 (VSS), MICROSD.9 (GND_1), MICROSD.10 (GND_2), MICROSD.11 (GND_3), MICROSD.12 (GND_4), MS1.4 (GND), R2.1, R8.1, RTC.2 (VCC), RTC.5 (NC_2), RTC.6 (NC_3), RTC.7 (NC_4), RTC.8 (NC_5), RTC.9 (NC_6), RTC.10 (NC_7), RTC.11 (NC_8), RTC.12 (NC), RTC.13 (GND), SWITCH.4, TEST-GND.1, TEST-GND1.1, TO_POWER_BOARD.3, TO_POWER_BOARD.4, U$3.3 (GND), VREG.2 (GND)
HB_IN1: MS1.20 (GPIO6), TO_POWER_BOARD.10
HB_IN2: MS1.19 (GPIO5), TO_POWER_BOARD.11
unnamed: B2.+, C3.1, RTC.14 (VBAT)
unnamed: P_MOS.3 (D), R4.2
unnamed: LED.2, LED1.A, R4.1
unnamed: FERRITEBEAD.P$1 (1), GND_JUMPER.2, TO_SENSOR_BOARD2.6
unnamed: LED2.A, R11.1
unnamed: CBOOT.1, VREG.1 (CB)
unnamed: CBOOT.2, D3.C, L1.1, VREG.6 (SW)
RTC_INT: EXTERNAL_INT.2, MS1.6 (GPIOA1), RTC.3 (!INT/SQW), SWITCH.3, TO_SENSOR_BOARD2.5
SCK: MICROSD.5 (CLK), MS1.11 (GPIOSCK)
SCL: MS1.18 (GPIOSCL), R3.1, RTC.16 (SCL), TO_SENSOR_BOARD1.1
SDA: MS1.17 (GPIOSDA), R5.1, RTC.15 (SDA), TO_SENSOR_BOARD1.2
SENSOR1: MS1.8 (GPIOA3), TO_SENSOR_BOARD1.5
SENSOR2: MS1.9 (GPIOA4), TO_SENSOR_BOARD1.6
SHIFT_CLK: MS1.23 (GPIO11), TO_POWER_BOARD.7
SHIFT_DATA: MS1.24 (GPIO12), TO_POWER_BOARD.6
SHIFT_LATCH: MS1.21 (GPIO9), TO_POWER_BOARD.9
SHUTDOWN: C2.2, D-FLIPFLOP.1 (CLK), MS1.5 (GPIOA0), R8.2
WAKE_NOSLEEP: MS1.10 (GPIOA5), P_MOS.1 (G), SWITCH.2

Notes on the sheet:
No Sleep LED
Feather M0 Wifi
To Sleep Switch
Voltage Divider To measure Battery voltage
Primary Power is from Battery Need Decoupling Cap on Vbat Vcc to GND
Measured: 2.2V
Connected in normal operation
N_Mosfet
Diode between !CLR and 2.2VCC makes pull up voltage fluxtuate between 3.4V -> 4.8V
Input voltage ripple is 7.14mV
L > 6.8 uH, Imax > 1.6A
Regulated 5V / USB Switch
Need Pull up to VCC for RTC_INT

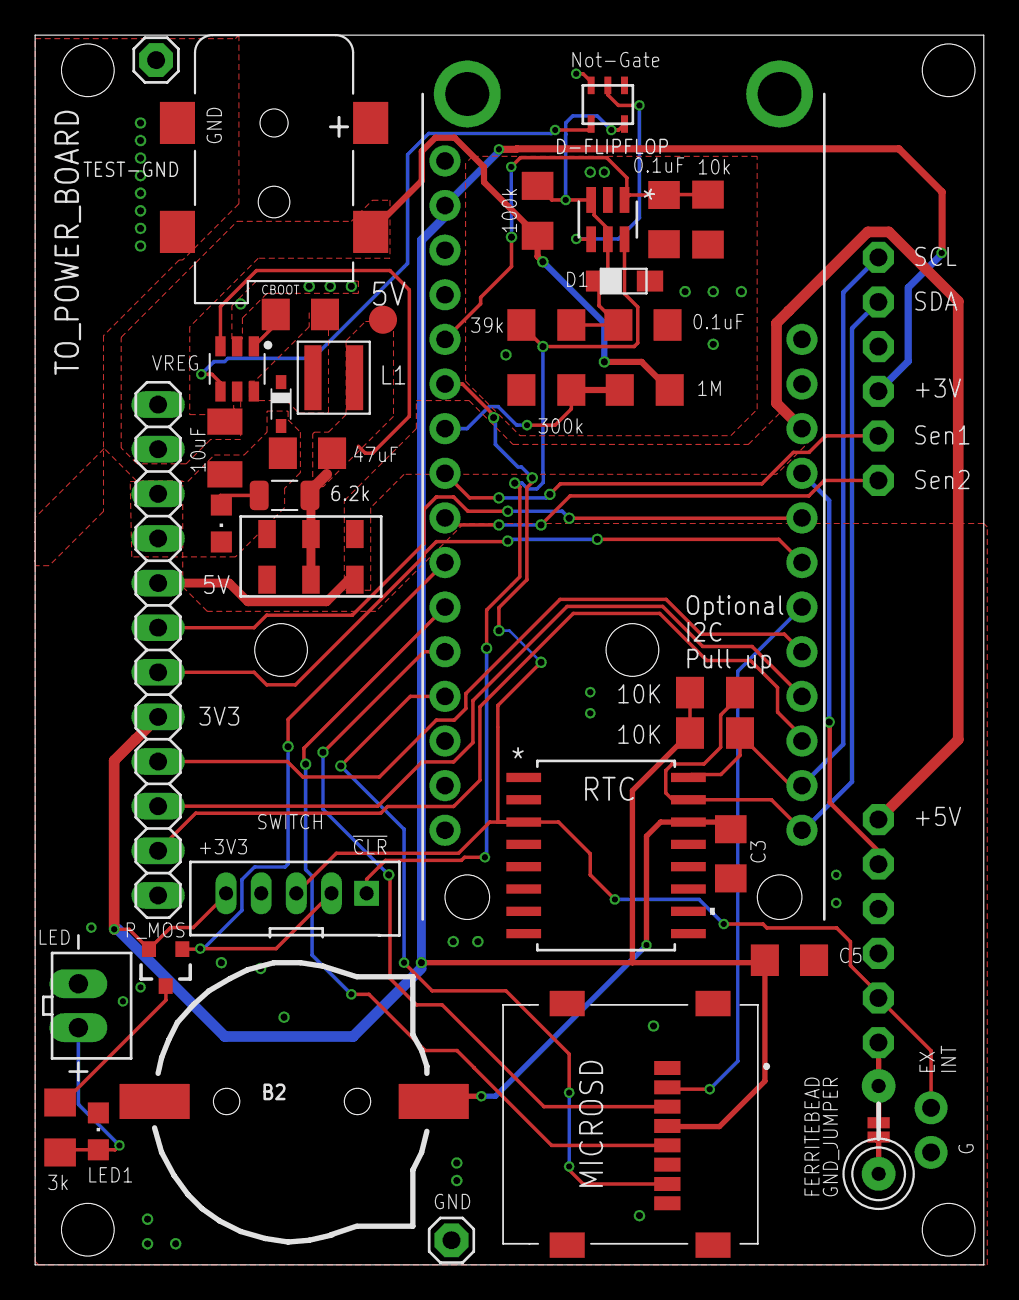
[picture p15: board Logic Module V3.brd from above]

Board: 2 copper layers, 54.0 x 70.0 mm, 43 parts (1 on the bottom side), 34 nets.

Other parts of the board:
U$2: OPENS-LOGO

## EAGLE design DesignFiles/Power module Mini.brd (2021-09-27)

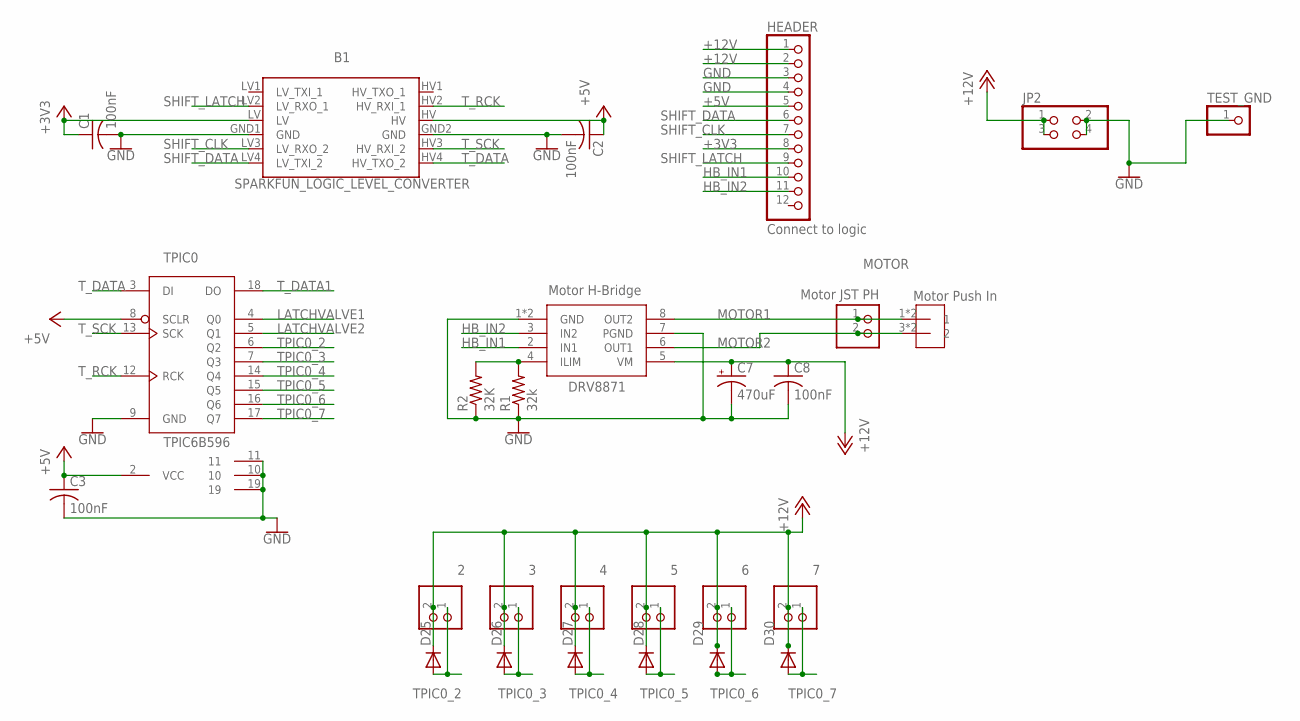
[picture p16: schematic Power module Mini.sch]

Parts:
2, 3, 4, 5, 6, 7: 2.5MM_JST_UP_2POS; JST_2POS_2.5MM_UP
B1: SPARKFUN_LOGIC_LEVEL_CONVERTER
C1, C2, C3, C8: 100nF; C1206
C7: 470uF; 140CLH-0810
D25, D26, D27, D28, D29, D30: DIODESOD-123; SOD-123
DRV8871: Motor H-Bridge; SOP8
HEADER: Connect to logic; 1X12
JP2: PINHD-2X2; 2X02
MOTOR: Motor JST PH; JST_2POS_2.5MM_UP
R1: 32k; 0204/5
R2: 32K; R0805
TEST_GND: PINHD-1X1; 1X01
TPIC0: TPIC6B596; DIP20
U$1: Motor Push In; 3.5MM_DIP2

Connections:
+3V3: B1.LV, C1.1, HEADER.8
+5V: B1.HV, C2.1, C3.1, HEADER.5, TPIC0.2 (VCC), TPIC0.8 (SCLR)
+12V: 2.2, 3.2, 4.2, 5.2, 6.2, 7.2, C7.+, C8.1, D25.C, D26.C, D27.C, D28.C, D29.C, D30.C, DRV8871.5 (VM), HEADER.1, HEADER.2, JP2.1, JP2.3
GND: B1.GND1 (GND), B1.GND2 (GND), C1.2, C2.2, C3.2, C7.-, C8.2, DRV8871.1 (GND), DRV8871.7 (PGND), DRV8871.GND, HEADER.3, HEADER.4, JP2.2, JP2.4, R1.1, R2.1, TEST_GND.1, TPIC0.9 (GND), TPIC0.10, TPIC0.11, TPIC0.19
HB_IN1: DRV8871.2 (IN1), HEADER.10
HB_IN2: DRV8871.3 (IN2), HEADER.11
LATCHVALVE1: TPIC0.4 (Q0)
LATCHVALVE2: TPIC0.5 (Q1)
MOTOR1: DRV8871.8 (OUT2), MOTOR.1, U$1.1, U$1.2 (1)
MOTOR2: DRV8871.6 (OUT1), MOTOR.2, U$1.3 (2), U$1.4 (2)
unnamed: DRV8871.4 (ILIM), R1.2, R2.2
SHIFT_CLK: B1.LV3 (LV_RXO_2), HEADER.7
SHIFT_DATA: B1.LV4 (LV_TXI_2), HEADER.6
SHIFT_LATCH: B1.LV2 (LV_RXO_1), HEADER.9
TPIC0_2: 2.1, D25.A, TPIC0.6 (Q2)
TPIC0_3: 3.1, D26.A, TPIC0.7 (Q3)
TPIC0_4: 4.1, D27.A, TPIC0.14 (Q4)
TPIC0_5: 5.1, D28.A, TPIC0.15 (Q5)
TPIC0_6: 6.1, D29.A, TPIC0.16 (Q6)
TPIC0_7: 7.1, D30.A, TPIC0.17 (Q7)
T_DATA: B1.HV4 (HV_TXO_2), TPIC0.3 (DI)
T_DATA1: TPIC0.18 (DO)
T_RCK: B1.HV2 (HV_RXI_1), TPIC0.12 (RCK)
T_SCK: B1.HV3 (HV_RXI_2), TPIC0.13 (SCK)

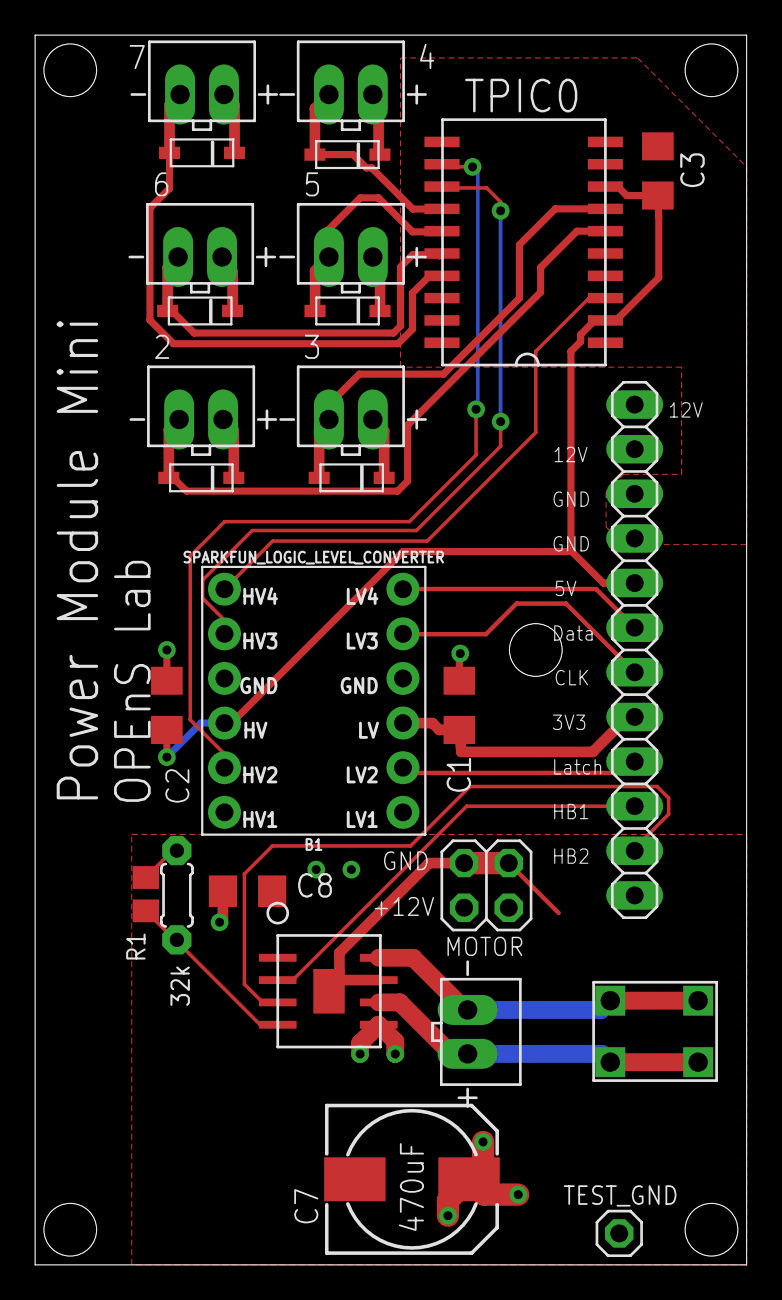
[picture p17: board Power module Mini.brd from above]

Board: 2 copper layers, 40.5 x 70.0 mm, 27 parts (0 on the bottom side), 21 nets.

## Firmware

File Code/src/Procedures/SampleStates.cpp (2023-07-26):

#include <Procedures/SampleStates.hpp>
#include <Application/Application.hpp>
#include <time.h>
#include <sstream>
#include <String>

bool pumpOff = 1;
bool flushVOff = 1;
bool sampleVOff = 1;

CSVWriter csvw{"data.csv"};

void writeLatch(bool controlPin, ShiftRegister & shift) {
	shift.setPin(controlPin, HIGH);
	shift.write();
	delay(80);
	shift.setPin(controlPin, LOW);
	shift.write();
}

// Idle
void SampleStateIdle::enter(KPStateMachine & sm) {
	Application & app = *static_cast<Application *>(sm.controller);
	if (app.sm.current_cycle < app.sm.last_cycle)
		setTimeCondition(time, [&]() { sm.transitionTo(SampleStateNames::ONRAMP); });
	else
		sm.transitionTo(SampleStateNames::FINISHED);
}

// Stop
void SampleStateStop::enter(KPStateMachine & sm) {
	Application & app = *static_cast<Application *>(sm.controller);
	app.pump.off();
	sample_end_time = millis();
	print("sample_end_time ms;;;");
	println(sample_end_time);
	pumpOff = 1;
	println("Pump off");

	app.shift.writeAllRegistersLow();
	app.shift.writeLatchOut();
	flushVOff = 1;
	sampleVOff = 1;

	//get and print to SD pressure after pump and valves are off
	current_pressure = app.pressure_sensor.getPressure();
	print("End pressure: ");
	println(current_pressure);
	char press_string[50];
	sprintf(press_string, "%d",current_pressure);
	const auto timenow = now();
	std::stringstream ss;
	ss << timenow;
	std::string time_string = ss.str();
	char cycle_string[50];
	sprintf(cycle_string, "%u", (int)app.sm.current_cycle);
	std::string strings[5] = {time_string,",Ending pressure for cycle: ",cycle_string,",,, ", press_string};
	csvw.writeStrings(strings, 5);

	setTimeCondition(time, [&]() { sm.next();});
}

void SampleStateOnramp::enter(KPStateMachine & sm) {
	Application & app = *static_cast<Application *>(sm.controller);
	const auto timenow = now();
	std::stringstream ss;
	ss << timenow;
	std::string time_string = ss.str();
	print("Starting cycle number;");
	println(app.sm.current_cycle);
	char cycle_string[50];
	sprintf(cycle_string, "%u", (int)app.sm.current_cycle);
	std::string strings[3] = {time_string,",Starting cycle ", cycle_string};
	csvw.writeStrings(strings, 3);

	if (flushVOff){
		app.shift.setAllRegistersLow();
		app.shift.setPin(TPICDevices::FLUSH_VALVE, HIGH);  // write in skinny
		app.shift.write();								   // write shifts wide*/
		flushVOff = 0;
		println("Flush valve turning on");
		sampleVOff = 1;
	}

	setTimeCondition(time, [&]() { sm.next();});
}

// Flush
void SampleStateFlush::enter(KPStateMachine & sm) {
	Application & app = *static_cast<Application *>(sm.controller);

	if (flushVOff){
		app.shift.setAllRegistersLow();
		app.shift.setPin(TPICDevices::FLUSH_VALVE, HIGH); // write in skinny
		app.shift.write();								   // write shifts wide*/
		flushVOff = 0;
		println("Flush valve turning on");
		sampleVOff = 1;
	}

	if (pumpOff){
		app.pump.on();
		pumpOff = 0;
		println("Pump on");
	}

	setTimeCondition(time, [&]() { sm.next();});
}

// Sample
void SampleStateSample::enter(KPStateMachine & sm) {
	Application & app = *static_cast<Application *>(sm.controller);
	float current_tare = app.sm.getState<SampleStateLoadBuffer>(SampleStateNames::LOAD_BUFFER).current_tare;

	if (sampleVOff){
		app.shift.setAllRegistersLow();
		app.shift.setPin(TPICDevices::WATER_VALVE, HIGH);
		app.shift.write();
		sampleVOff = 0;
		println("Sample valve turning on");
		flushVOff = 1;
	}

	const auto timenow = now();
	std::stringstream ss;
	ss << timenow;
	std::string time_string = ss.str();
	char cycle_string[50];
	sprintf(cycle_string, "%u", (int)app.sm.current_cycle);
	std::string strings[3] = {time_string, ",Sample Start Cycle: ", cycle_string};
	csvw.writeStrings(strings, 3);
	sample_start_time = millis();
	print("sample_start_time ms ;;;");
	println(sample_start_time);

	if (pumpOff){
		app.pump.on();
		pumpOff = 0;
		println("Pump on");
	}

	auto const condition = [&]() {
		load = 0;
		load_rate = 0;
		// check load, exit if matching mass
		new_load = app.load_cell.getLoad(1);
		new_time = millis();
		print("New mass reading;");
		println(new_load);
		print("New time;;;");
		println(new_time);
		// compensate for poor measurements for first 4 (s2) or first 5(sampler1)
		if(load_count==wt_offset_load_count){
			wt_offset = ((new_load - prior_load)/(new_time - prior_time))*(new_time - sample_start_time);
			print("Weight offset;;;;");
			println(wt_offset);
		}
		
		const auto timenow = now();
		std::stringstream ss;
		ss << timenow;
		std::string time_string = ss.str();
		char cycle_string[50];
		sprintf(cycle_string, "%u", (int)app.sm.current_cycle);
		load = new_load - current_tare >= mass - wt_offset;
		if (load){
			std::string temp[3] = {time_string,",Ended due to load cycle: ",cycle_string};
			csvw.writeStrings(temp, 3);
			println("Sample state ended due to: load ");
			pressureEnded = 0;
			return load;
		}

			//if not exiting due to sample load, check overall load, time and exit if over time
		else{
			// check load reading relative to cap of 2900 g
			total_load = 0;
			total_load = new_load > 2900;
			if (total_load){
				std::string temp[4] = {time_string,",Ended due to total load cycle: ",cycle_string};
				csvw.writeStrings(temp, 4);
				println("Sample state ended due to: total load ");
				pressureEnded = 0;
				// trigger end of all sampling
				app.sm.current_cycle = app.sm.last_cycle;
				return total_load;
			}
			
			t_max = timeSinceLastTransition() >= secsToMillis(time);
			t_adj = timeSinceLastTransition() >= time_adj_ms;
			if (t_max || t_adj){
				std::string temp[4] = {time_string,",Ended due to time cycle: ",cycle_string};
				csvw.writeStrings(temp, 4);
				println("Sample state ended due to: time");
				pressureEnded = 0;
				return t_max || t_adj;
			}
			//if not exiting due to load and time, check pressure
			else{
				pressure = !app.pressure_sensor.isWithinPressure();
				if (pressure){
					std::string temp[4] = {time_string, ",Ended due to pressure cycle: ",cycle_string};
					csvw.writeStrings(temp, 4);
					println("Sample state ended due to: pressure");
					pressureEnded = 1;
					return pressure;
				}
				//if not exiting due to load, time, and pressure, check pumping rate
				else{
					if (load_count > 0){
						// check in to see if load increase is really slow meaning getting a lot of air or load not reading
						// after first 25 samples, should be different from tare		
						if (load_count== 25){
									load_check += new_load;
									load_check = load_check/(load_count) - current_tare;
									print("Load rate check value: ");
									println(load_check);
									print("current tare: ");
									println(current_tare);
									load_check = 0;
									load_rate = abs(load_check - current_tare) < 0.01;
									if (load_rate){
										std::string temp[4] = {time_string, ",Ended due to low load rate: ",cycle_string};
										csvw.writeStrings(temp, 4);
										println("Sample state ended due to: low load rate");
										pressureEnded = 0;
										return load_rate;
									}
								}
						else if (load_count <25){
							load_check += new_load;
							print("Load check ");
							print(load_check);
							print(" for load count ");
							println(load_count);
							}
						accum_load = new_load - current_tare;
						accum_time = new_time - sample_start_time;
						avg_rate = 1000*(accum_load/accum_time);
						print("Average rate in g/s;;;;");
						println(avg_rate,4);

						//check to see if sampling time is appropriate
						print("Coded time remaining in millis;;;");
						code_time_est = time_adj_ms - timeSinceLastTransition();
						println(code_time_est);
						// update time if more than 10% off and new load - tare > 1
						if (load_count > 5){
							if (new_load - current_tare > 1){
								weight_remaining = mass - (new_load - current_tare);
								print("Weight remaining (mass - (new_load - current_tare));");
								println(weight_remaining);
								// calculate new time based upon average rate
								new_time_est = weight_remaining/((new_load - current_tare)/(new_time - sample_start_time));
								print("Estimated time remaining in ms: weight_remaining/average rate;;;");
								println(new_time_est);
								if (abs((code_time_est - new_time_est)/code_time_est) > 0.1){
									time_adj_ms = new_time_est + timeSinceLastTransition();
									print("Code time outside 10 percent of estimated time. Updated sampling time in millis;;;");
									println(time_adj_ms);
								}
							}
						}
					}
					prior_load = new_load;
					prior_time = new_time;
					prior_rate = new_rate;
					prior_time_est = new_time_est;
					load_count += 1;
					return load || total_load || t_max || t_adj || pressure || load_rate;
					}
				}
			}
	};
	setCondition(condition, [&]() { sm.next();});
}

// Sample leave
void SampleStateSample::leave(KPStateMachine & sm) {
	Application & app = *static_cast<Application *>(sm.controller);
}

// Finished
void SampleStateFinished::enter(KPStateMachine & sm) {
	Application & app = *static_cast<Application *>(sm.controller);
	app.led.setFinished();
	app.sm.reset();
}

// Setup
void SampleStateSetup::enter(KPStateMachine & sm) {
	Application & app = *static_cast<Application *>(sm.controller);
	app.led.setRun();
	//get and print time
	const auto timenow = now();
	std::stringstream ss;
	ss << timenow;
	std::string time_string = ss.str();
	std::string strings[2] = {time_string, ",New Sampling Sequence"};
	csvw.writeStrings(strings, 2);
	setTimeCondition(time, [&]() { sm.next();});
}

void SampleStateBetweenPump::enter(KPStateMachine & sm) {
	Application & app = *static_cast<Application *>(sm.controller);
	app.pump.off();
	pumpOff = 1;
	println("Pump off");
	setTimeCondition(time, [&]() { sm.next();});
}

void SampleStateBetweenValve::enter(KPStateMachine & sm) {
	Application & app = *static_cast<Application *>(sm.controller);
	
	if (sampleVOff){
		app.shift.setAllRegistersLow();
		app.shift.setPin(TPICDevices::WATER_VALVE, HIGH);
		app.shift.write();
		sampleVOff = 0;
		println("Sample valve turning on");
		flushVOff = 1;
	}
	setTimeCondition(time, [&]() { sm.next();});
}

void SampleStateFillTubeOnramp::enter(KPStateMachine & sm) {
	Application & app = *static_cast<Application *>(sm.controller);

	if (flushVOff){
		app.shift.setAllRegistersLow();
		app.shift.setPin(TPICDevices::FLUSH_VALVE, HIGH);// write in skinny
		app.shift.write();								   // write shifts wide*/
		flushVOff = 0;
		println("Flush valve turning on");
		sampleVOff = 1;
	}
	setTimeCondition(time, [&]() { sm.next();});
}

void SampleStateFillTube::enter(KPStateMachine & sm) {
	Application & app = *static_cast<Application *>(sm.controller);

	if (flushVOff){
		app.shift.setAllRegistersLow();
		app.shift.setPin(TPICDevices::FLUSH_VALVE, HIGH); // write in skinny
		app.shift.write();								   // write shifts wide*/
		flushVOff = 0;
		println("Flush valve turning on");
		sampleVOff = 1;
	}
	if (pumpOff){
		app.pump.on();
		pumpOff = 0;
		println("Pump on");
	}

	setTimeCondition(time, [&]() { sm.next();});
}

void SampleStatePressureTare::enter(KPStateMachine & sm) {
	Application & app = *static_cast<Application *>(sm.controller);
	if (flushVOff){
		app.shift.setAllRegistersLow();
		app.shift.setPin(TPICDevices::FLUSH_VALVE, HIGH);  // write in skinny
		app.shift.write();								   // write shifts wide*/
		flushVOff = 0;
		println("Flush valve turning on");
		sampleVOff = 1;		
	}
	if (pumpOff){
		app.pump.on();
		pumpOff = 0;
		println("Pump on");
	}

	sum	  = 0;
	count = 0;

	setTimeCondition(time, [&]() { sm.next();});
}

void SampleStatePressureTare::update(KPStateMachine & sm) {
	Application & app = *static_cast<Application *>(sm.controller);
	sum += app.pressure_sensor.getPressure();
	++count;
}
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

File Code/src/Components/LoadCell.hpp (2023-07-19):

#pragma once
#include <KPFoundation.hpp>
#include <ADS1232.h>
#include <time.h>
#include <Application/Constants.hpp>
#include <FileIO/CSVWriter.hpp>
#include <String>
#include <sstream>

#define _dout HardwarePins::DOUT
#define _sclk HardwarePins::SCLK
#define _pdwn HardwarePins::PDWN

class LoadCell : public KPComponent {
public:
	CSVWriter csvw{"data.csv"};
	ADS1232 weight = ADS1232(_pdwn, _sclk, _dout);
	float tare;
	float factor = 0.002348;//0.002348 sampler1; 0.002192 sampler2
	float offset = -19857.150;// -19857.150 sampler1; -18344.85 sampler2
	long reading = 0;
	long sum;
	short count;

	LoadCell(const char * name, KPController * controller)
		: KPComponent(name, controller) {}
	void setup() override {
		weight.power_up();
		// reset library values to default
  		weight.OFFSET = 0;
  		weight.SCALE = 1.0;
		tare = 0;

		print("Initial load;");
		println(reTare(50));
	}
	long read(int qty) {
		//println("in read");

		println();
		sum = 0;
		count = 0;
		//display every reading
		for (int i = 0; i < qty; ++i) {
			reading = weight.raw_read(1);
			#ifdef LOAD_CAL
				print("Load reading;");
				print(i);
				print(";");
				println(reading);
			#endif
				if (qty>4){
					//don't include first 5 readings in average due to unreliability
					if (i>3){
						sum += reading;
						count ++;
					}
				}
				//if there aren't more than 5 readings, just use all of them
				else {
					sum += reading;
					count ++;
				}
			}
			reading = sum/(count);

		return reading;
	}

	float getLoad(int qty) {
		// gets factor and offset from this file during setup, gets factor and offset from SD after
		return factor * read(qty) + offset;
	}

	float getLoadPrint(int qty) {
		float load = getLoad(qty);
		char load_string[50];
		sprintf(load_string, "%d.%02u", (int)load, (int)((load - (int)load) * 100));
		std::string strings[2] = {"FLAGGED LOAD, ", load_string};
		csvw.writeStrings(strings, 2);
		println("FLAGGED LOAD;", load_string);
		return load;
	}

	float reTare(int qty) {
		tare = getLoad(qty);
		return tare;
	}

	float getTaredLoad(int qty) {
		return getLoad(qty) - tare;
	}

	long getVoltage() {
		return weight.raw_read(1);
	}

	float readGrams() {
		return factor * (long)weight.raw_read(1) + offset;
	}
};

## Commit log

2021-09-27 Initial design files upload
    [AcrylicCircle.dxf, LED Box.stl, LED Lid.stl, Load cell.stl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]
2021-09-28 added logic module pcbs
    [Logic Module V3.brd, Logic Module V3.sch]
2022-06-20 Additional PCBs
    Added ADS1232 and pressure sensor PCBs. Removed sensor pcb
    [ADS1232 interface.brd, ADS1232 interface.sch, Load cell.stl, Sensor module.brd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]
2022-06-20 Added code
    [log.csv]
2023-06-29 Added new battery hole to AcrylicCircle
2023-07-19 Updated to match single sampler, removed commented out lines
    [log.csv]
2023-07-25 wt offset adjusted for sampler 1

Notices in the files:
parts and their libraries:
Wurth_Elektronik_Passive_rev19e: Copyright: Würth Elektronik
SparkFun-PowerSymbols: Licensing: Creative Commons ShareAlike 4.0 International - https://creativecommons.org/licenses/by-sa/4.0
